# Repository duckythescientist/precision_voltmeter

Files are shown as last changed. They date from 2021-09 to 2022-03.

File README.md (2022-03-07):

# Precision Voltmeter

Partly based off of the Scullcom millivolt meter: http://www.scullcom.uk/design-build-6%c2%bd-digit-millivolt-meter-part-1/

## Serial comms

```
Commands:
    h    - Print this help
    ?    - Print version and date
    r    - Toggle live readout over serial
    p    - Print calibration
    z    - Calibrate at 0V (inputs shorted)
    c... - Calibrate for a specific range and value

Calibration:
    c[n]:[f]  - Calibrates for range [n] with external applied voltage [f]
    Range:
        0: x1 LV
        1: x10
        2: x100
        3: x1000
    Example: to calibrate the x10 range (HV input) with a 4.123V reference,
        the command would be `c1:4.123`
```

# Improvement notes

I added an opto-isolated serial output and spent a weekend tearing down and building back up the circuit. I don't think it's going to get much better than it is (or already was). Without ESD/EMI and environmental noise, the noise in the readings is on the same order of magnitude that I'd expect from thermal noise of a 1Meg resistor. Assuming that my napkin math is correct. Also, the constant offset that I'm seeing is also on the order of what's to be expected with the input bias current of the LTC2057 and a 1Meg resistor. I guess it's just up to software corrections. Still getting around 19-20 usable bits from the ADC. I'm calling that a win.

Environmental noise is still a big issue. Stddev of the readings lowers by an order of magnitude if I sit perfectly still.

# Notes for Future Versions and Improvements

## Issues

The LTC2057 has a common-mode input range from 0.1V below V- to 1.5V _below_ V+. Meaning that with a -2.5V,+5V supply, I can only buffer signals up to 3.5V technically. I'm seeing some sort of latchup-type behavior at around 4.2V. I've bodged in a 6.8V supply rail to the op-amp.

## Bodges

The sampling of the ADC is rather noisy. Adding filter capacitors right at the input and the vref seem to help. Reduced the resistor between the buffer and the ADC to 2.2k. May want to go lower? I'm currently at 100R series from the buffer to the ADC and a 2.2nF cap to gnd.

Adding extra voltage regulator to drive the op-amp positive rail at around 6.8V to give enough common-mode headroom to buffer a full input swing to the ADC.

## Future

The x10 mode presents around a 1Meg input impedance to the op-amp this combined with the couple hundred pA of input bias and offset results in a couple hundred microvolts of DC offset. This has a minimal temperature coefficient up to about 75C but does have a common-mode voltage dependence. I'm not sure what to do to fix it.

A 1Meg input impedance may be the way to go.

For lower noise, it may be nice to try LT3094 and LT3042 for post switching converter regulation. The switching regulator. However, the voltage lines look pretty clean right now. Also, these regulators are pretty expensive and are DFN packages. UPDATE: replacing the switching regulator with batteries didn't measurably reduce the noise. The current design is good enough.

A metal enclosure and/or more shielding could maybe help with environmental noise.

I need a buffer amp for the output of my Kelvin-Varley divider. Or I need a voltage reference below about 4V to calibrate the x1 range. This is a lab problem and not a problem of the voltmeter.

I need to investigate Barbouri's v2 design and see if there is anything worth adding to my design.

# References

## App Notes

Shielding and guarding: https://www.analog.com/media/en/technical-documentation/application-notes/41727248an_347.pdf

Staying well grounded: https://www.analog.com/en/analog-dialogue/articles/staying-well-grounded.html

Millivolt meter PCB: https://www.barbouri.com/2016/05/26/millivolt-meter/ and https://www.barbouri.com/2019/08/07/millivolt-meter-version-2/

EMI filtering for DC-DC converters: https://www.ti.com/lit/an/snva489c/snva489c.pdf

Ferrite beads demystified: https://www.analog.com/en/analog-dialogue/articles/ferrite-beads-demystified.html

Shielding and guarding: https://www.analog.com/media/en/technical-documentation/application-notes/41727248an_347.pdf

PCB guidelines for reduced EMI: https://www.ti.com/lit/an/szza009/szza009.pdf

Overvoltage protection for sensitive amplifier applications: https://www.maximintegrated.com/en/design/technical-documents/app-notes/4/4035.html

Switching low-level signals to a DMM: https://www.ni.com/en-us/innovations/white-papers/06/switching-low-level-signals-to-a-dmm.html

## Datasheets

Voltage reference, ADR4540, used in Scullcom's meter: https://www.analog.com/media/en/technical-documentation/data-sheets/ADR4520_4525_4530_4533_4540_4550.pdf

Voltage reference, MAX6126, used in my meter, kelvin connections: https://datasheets.maximintegrated.com/en/ds/MAX6126.pdf

Negative adjustable voltage regulator, LM337L: https://www.ti.com/lit/ds/symlink/lm337l.pdf

HV low noise zero-drift op-amp, LTC2057, used in my meter: https://www.analog.com/media/en/technical-documentation/data-sheets/2057f.pdf

Zero-drift single-supply rail-to-rail op-amp, AD8628, used in Scullcom's meter: https://www.analog.com/media/en/technical-documentation/data-sheets/AD8628_8629_8630.pdf

ADC 24-bit, LTC2400: https://www.analog.com/media/en/technical-documentation/data-sheets/2400fa.pdf

SPI digital isolator, ADuM3152: https://www.analog.com/media/en/technical-documentation/data-sheets/ADuM3151_3152_3153.pdf

ATmega32U4: https://ww1.microchip.com/downloads/en/DeviceDoc/Atmel-7766-8-bit-AVR-ATmega16U4-32U4_Datasheet.pdf

## Software

64-bit floating point library for AVR-8: https://fp64lib.org/documentation/fp64lib-library-reference/ and https://github.com/fp64lib/fp64lib

MAX7219 7-seg LED driver library: https://github.com/JemRF/max7219

PinChangeInterrupt: https://github.com/NicoHood/PinChangeInterrupt

Statistics library for Arduino: https://github.com/RobTillaart/Statistic

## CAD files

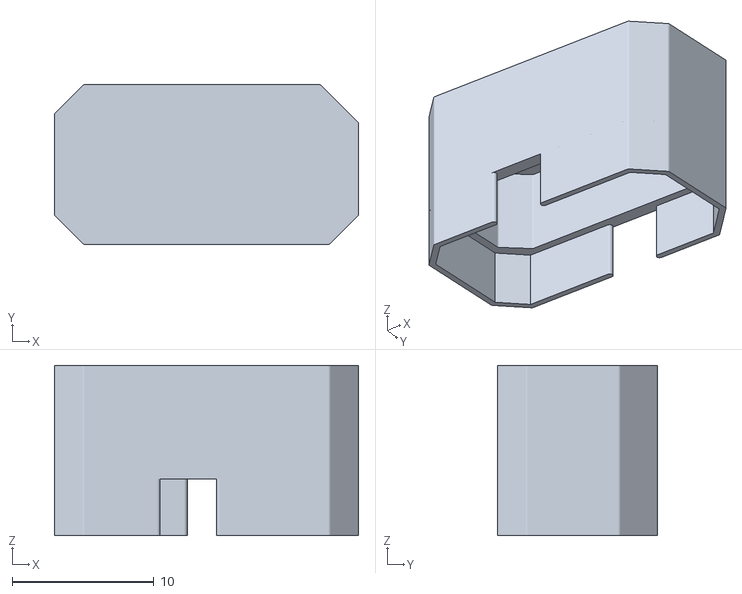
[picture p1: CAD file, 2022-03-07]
vref_cover/vref_cover.stl
21.4 x 11.3 x 12.0

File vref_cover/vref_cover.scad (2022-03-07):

file = "precision_voltmeter-Eco1_User.svg";
ax = 20.64;
ay = 10.79;

offset_r = 0.23;
$fn=100;
difference() {
    translate([-110.48, -112.22, 0]) {
        union() {
            linear_extrude(12)
                offset(r=offset_r)
                    import(file);
            translate([0, 0, 4])
                hull()
                    linear_extrude(8)
                        offset(r=offset_r)
                            import(file);
        }
    }
    #scale([18.5/ax, 8.7/ay, 1 - 2/12])
    translate([-110.48, -112.22, 0]) {
        hull()
            linear_extrude(12)
                offset(r=offset_r)
                    import(file);
    }
}

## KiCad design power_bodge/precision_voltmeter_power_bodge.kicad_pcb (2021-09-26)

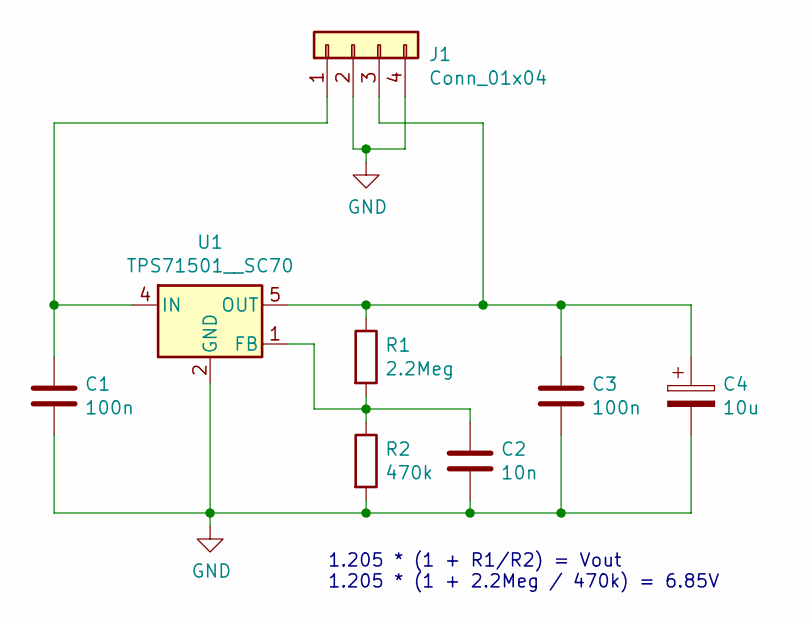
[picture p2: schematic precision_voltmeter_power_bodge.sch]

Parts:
C1, C3: 100n; C_0805_2012Metric_Pad1.18x1.45mm_HandSolder
C2: 10n; C_0805_2012Metric_Pad1.18x1.45mm_HandSolder
C4: 10u; C_0805_2012Metric_Pad1.18x1.45mm_HandSolder
J1: Conn_01x04; PinHeader_1x04_P2.54mm_Vertical
R1: 2.2Meg; R_0805_2012Metric_Pad1.20x1.40mm_HandSolder
R2: 470k; R_0805_2012Metric_Pad1.20x1.40mm_HandSolder
U1: TPS71501__SC70; SOT-353_SC-70-5

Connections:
GND: C1.2, C2.2, C3.2, C4.2, J1.2, J1.4, R2.2, U1.2 (GND)
unnamed: C1.1, J1.1, U1.4 (IN)
unnamed: C2.1, R1.2, R2.1, U1.1 (FB)
unnamed: C3.1, C4.1, J1.3, R1.1, U1.5 (OUT)

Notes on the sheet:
1.205 * (1 + R1/R2) = Vout 1.205 * (1 + 2.2Meg / 470k) = 6.85V

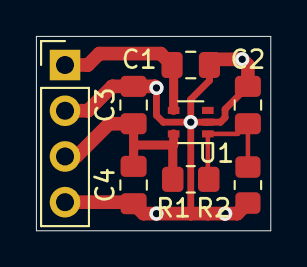
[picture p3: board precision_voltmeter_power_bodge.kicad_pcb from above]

Board: 2 copper layers, 13.0 x 10.8 mm, 8 parts (0 on the bottom side), 4 nets.

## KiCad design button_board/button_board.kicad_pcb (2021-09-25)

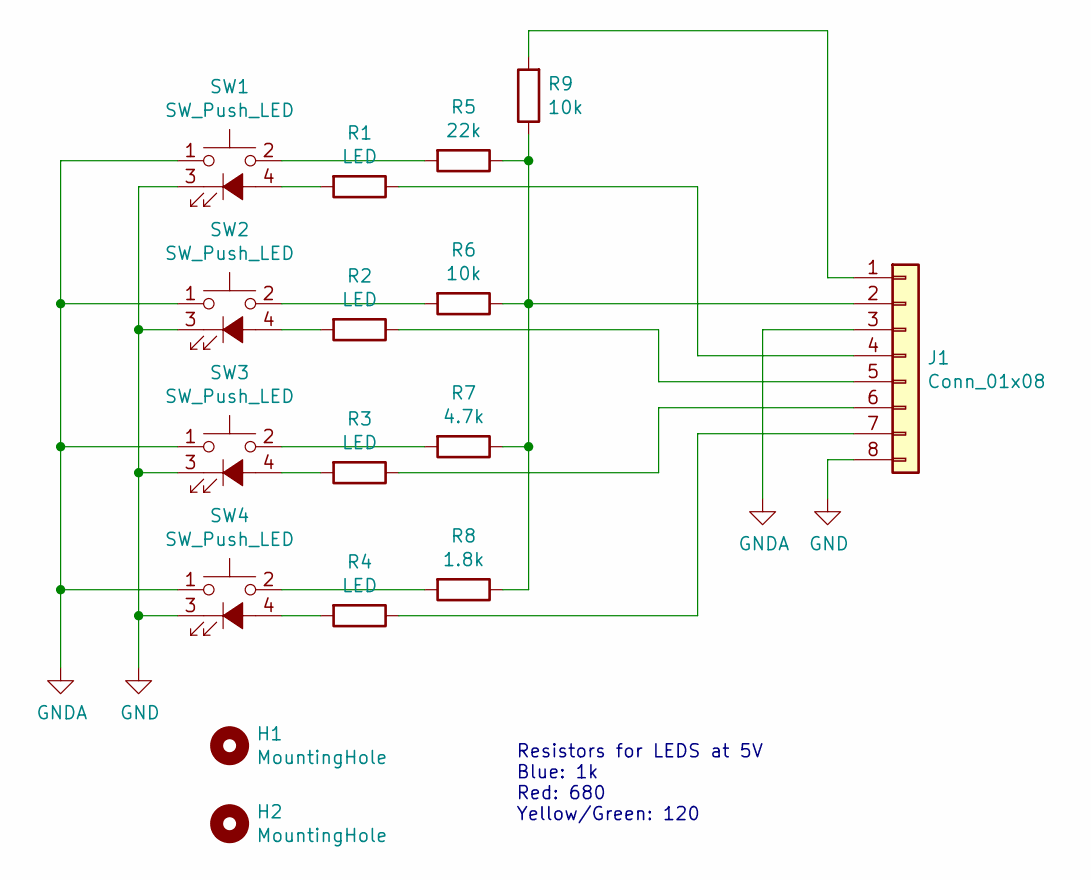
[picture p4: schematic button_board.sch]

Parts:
H1, H2: MountingHole; MountingHole_2.7mm_M2.5
J1: Conn_01x08; PinHeader_1x08_P2.54mm_Vertical
R1, R2, R3, R4: LED; R_0805_2012Metric_Pad1.20x1.40mm_HandSolder
R5: 22k; R_0805_2012Metric_Pad1.20x1.40mm_HandSolder
R6, R9: 10k; R_0805_2012Metric_Pad1.20x1.40mm_HandSolder
R7: 4.7k; R_0805_2012Metric_Pad1.20x1.40mm_HandSolder
R8: 1.8k; R_0805_2012Metric_Pad1.20x1.40mm_HandSolder
SW1, SW2, SW3, SW4: SW_Push_LED; tactile-push-button-illuminated_ILS_TA180

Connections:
GND: J1.8, SW1.3 (K), SW2.3 (K), SW3.3 (K), SW4.3 (K)
GNDA: J1.3, SW1.1, SW2.1, SW3.1, SW4.1
unnamed: J1.1, R9.2
unnamed: J1.2, R5.1, R6.1, R7.1, R8.1, R9.1
unnamed: J1.4, R1.1
unnamed: J1.5, R2.1
unnamed: J1.6, R3.1
unnamed: J1.7, R4.1
unnamed: R1.2, SW1.4 (A)
unnamed: R2.2, SW2.4 (A)
unnamed: R3.2, SW3.4 (A)
unnamed: R4.2, SW4.4 (A)
unnamed: R5.2, SW1.2
unnamed: R6.2, SW2.2
unnamed: R7.2, SW3.2
unnamed: R8.2, SW4.2

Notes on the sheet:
Resistors for LEDS at 5V Blue: 1k Red: 680 Yellow/Green: 120

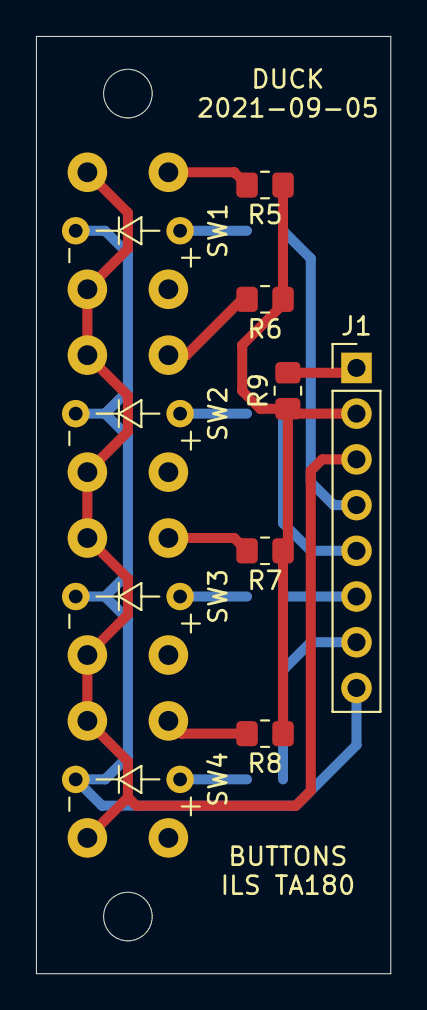
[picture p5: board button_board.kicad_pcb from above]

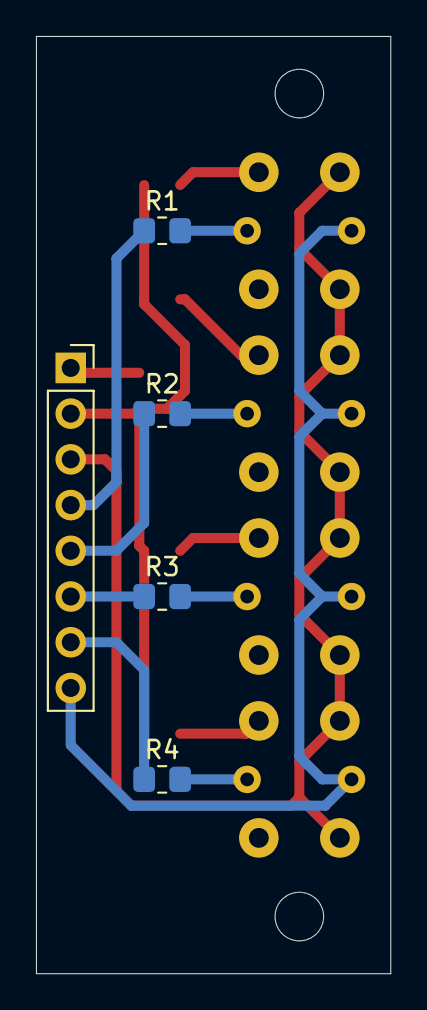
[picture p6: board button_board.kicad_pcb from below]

Board: 2 copper layers, 19.7 x 52.1 mm, 16 parts (4 on the bottom side), 16 nets.

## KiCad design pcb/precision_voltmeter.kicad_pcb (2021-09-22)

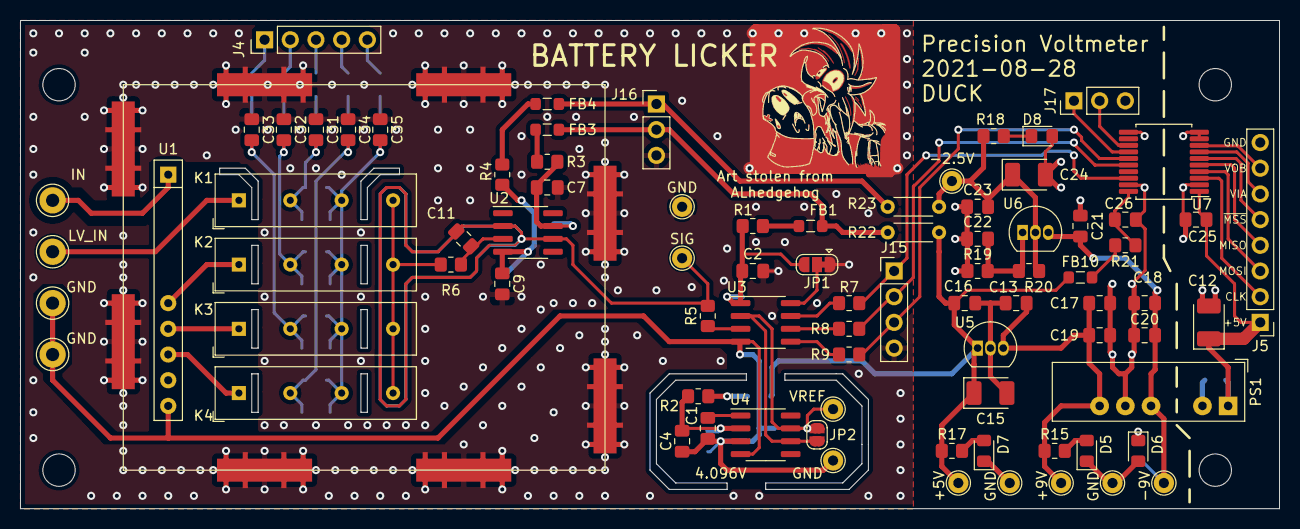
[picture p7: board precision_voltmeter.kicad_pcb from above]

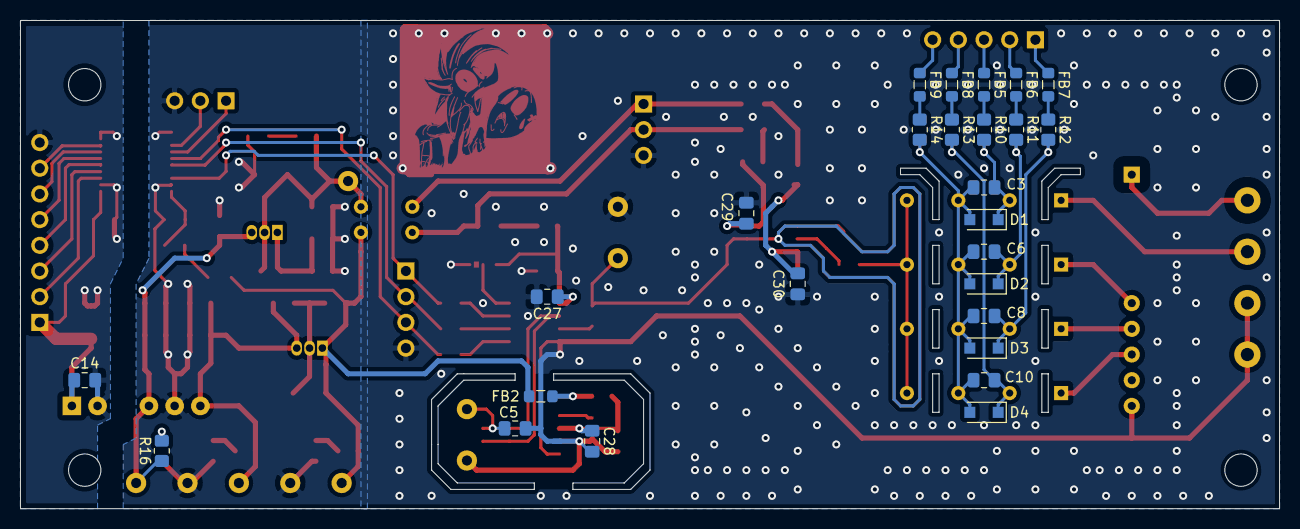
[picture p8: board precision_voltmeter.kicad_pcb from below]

Board: 2 copper layers, 124.5 x 48.3 mm, 121 parts (26 on the bottom side), 63 nets.

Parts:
C1, C2, C3, C4, C5, C6, C7, C8, C9, C10, C13, C14, C16, C19, C20, C21, C22, C23, C25, C26, C31, C32, C33, C34: 100n; C_0805_2012Metric_Pad1.18x1.45mm_HandSolder
C11: DNP 220p; C_0805_2012Metric_Pad1.18x1.45mm_HandSolder
C12, C15, C24: 4.7u; CP_EIA-3528-12_Kemet-T_Pad1.50x2.35mm_HandSolder
C17, C18: 1u; C_0805_2012Metric_Pad1.18x1.45mm_HandSolder
C27, C28, C29, C30: 10u; C_0805_2012Metric_Pad1.18x1.45mm_HandSolder
C35: 5x 100n; C_0805_2012Metric_Pad1.18x1.45mm_HandSolder
D1, D2, D3, D4: 1n4148; D_SOD-123F
D5, D6, D7, D8: LED; LED_0805_2012Metric_Pad1.15x1.40mm_HandSolder
FB1, FB2, FB3, FB4, FB5, FB6, FB7, FB8, FB9, FB10: Bead; L_0805_2012Metric_Pad1.05x1.20mm_HandSolder
H1, H2, H3, H4: MountingHole; MountingHole_3.2mm_M3
J1: IN_PLUS; Pin_D1.3mm_L11.0mm
J2, J14: IN_MINUS; Pin_D1.3mm_L11.0mm
J3: IN_PLUS_LV; Pin_D1.3mm_L11.0mm
J4: Conn_01x05; PinHeader_1x05_P2.54mm_Vertical
J5: Conn_01x08; PinHeader_1x08_P2.54mm_Vertical
J6, J7, J8, J9, J10, J11, J12, J13: shield clip; smt_rfi_clip_S2711-46R
J15: Conn_01x04; PinHeader_1x04_P2.54mm_Vertical
J16, J17: Conn_01x03; PinHeader_1x03_P2.54mm_Vertical
JP1: 50/60Hz select; SolderJumper-3_P1.3mm_Bridged12_RoundedPad1.0x1.5mm
JP2: Jumper_NO_Small; SolderJumper-2_P1.3mm_Open_RoundedPad1.0x1.5mm
K1, K2, K3, K4: COTO-1839-108N; Relay_SPST_StandexMeder_SIL_Form1A
PS1: 5V in +/-9V out; Converter_DCDC_XP_POWER-IAxxxxS_THT
R1, R2, R3, R4, R11, R12, R13, R14: 10R; R_0805_2012Metric_Pad1.20x1.40mm_HandSolder
R5: 4.7k; R_0805_2012Metric_Pad1.20x1.40mm_HandSolder
R6: 1.2k; R_0805_2012Metric_Pad1.20x1.40mm_HandSolder
R7, R8: 33; R_0805_2012Metric_Pad1.20x1.40mm_HandSolder
R9: 3x 33R; R_0805_2012Metric_Pad1.20x1.40mm_HandSolder
R10: 5x 10R; R_0805_2012Metric_Pad1.20x1.40mm_HandSolder
R15, R16: 1k; R_0805_2012Metric_Pad1.20x1.40mm_HandSolder
R17, R18: 470; R_0805_2012Metric_Pad1.20x1.40mm_HandSolder
R19, R20: 240; R_0805_2012Metric_Pad1.20x1.40mm_HandSolder
R21: 2.2R; R_0805_2012Metric_Pad1.20x1.40mm_HandSolder
R22, R23: 0; R_Axial_DIN0204_L3.6mm_D1.6mm_P5.08mm_Horizontal
TP1: vref; TestPoint_THTPad_D2.0mm_Drill1.0mm
TP2, TP3, TP4, TP6: gnd; TestPoint_THTPad_D2.0mm_Drill1.0mm
TP5: sig_buffered; TestPoint_THTPad_D2.0mm_Drill1.0mm
TP7, TP8, TP9, TP10: TestPoint; TestPoint_THTPad_D2.0mm_Drill1.0mm
U1: Caddock_resistor_network_1776-C68; R_Array_SIP10-6
U2: LTC2057/AD8628; SOIC-8_3.9x4.9mm_P1.27mm
U3: LTC2400CS8PBF; SOIC-8_3.9x4.9mm_P1.27mm
U4: MAX6126/ADR4540; SOIC-8_3.9x4.9mm_P1.27mm
U5: L78L05_TO92; TO-92_Inline
U6: LM337L_TO92; TO-92_Inline
U7: ADUM3152; SSOP-20_5.3x7.2mm_P0.65mm

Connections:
+5V: C15.1, C16.1, FB1.1, FB2.1, FB3.1, FB10.1, J16.2, R17.1, R22.1, R22.2, TP8.1, U5.1
+5VP: C12.1, C14.1, C25.1, J5.1, PS1.1, U7.1
+9V: C13.1, C17.1, C19.1, PS1.6, R15.1, TP7.1, U5.3
-2V5: C23.2, C24.1, FB4.1, J16.1, R18.1, R20.2, R23.1, R23.2, TP10.1, U6.2
-9V: C18.1, C20.1, C21.2, PS1.4, R16.1, TP9.1, U6.3
/VCC_ADC: C2.1, C27.1, JP1.3, R1.2, U3.1
/VCC_OPAMP: C7.1, C29.1, R3.2, U2.7
/VCC_REF: C4.1, C28.1, R2.2, U4.2
/VSS_OPAMP: C9.1, C30.1, R4.2, U2.4
GND: C1.2, C2.2, C4.2, C5.2, C7.2, C9.2, C13.2, C15.2, C16.2, C17.2, C18.2, C19.2, C20.2, C21.1, C22.1, C23.1, C24.2, C26.2, C27.2, C28.2, C29.2, C30.2, C31.1, C32.1, C33.1, C34.1, C35.1, D5.1, D6.2, D7.1, D8.2, J2.1, J6.1, J7.1, J8.1, J9.1, J10.1, J11.1, J12.1, J13.1, J14.1, J15.4, J16.3, J17.3, JP1.1, PS1.5, R19.1, TP2.1, TP3.1, TP4.1, TP6.1, U1.10, U3.4, U4.3, U4.4, U5.2, U7.11, U7.19
GNDPWR: C12.2, C14.2, C25.2, J5.8, PS1.2, U7.2, U7.9, U7.10
MISO: J15.2, R8.1, U7.16
unnamed: C1.1, U4.1
unnamed: C3.2, C31.2, D1.1, K1.3, R10.2
unnamed: C5.1, JP2.1, JP2.2, TP1.1, U3.2, U4.6, U4.7
unnamed: C3.1, C6.1, C8.1, C10.1, C35.2, D1.2, D2.2, D3.2, D4.2, K1.5, K2.5, K3.5, K4.5, R14.2
unnamed: C10.2, C34.2, D4.1, K4.3, R13.2
unnamed: C11.1, R5.2, TP5.1, U2.2, U2.6
unnamed: C11.2, R6.1, U2.3
unnamed: C22.2, R19.2, R20.1, U6.1
unnamed: C26.1, R21.2, U7.20
unnamed: C6.2, C32.2, D2.1, K2.3, R11.2
unnamed: C8.2, C33.2, D3.1, K3.3, R12.2
unnamed: D5.2, R15.2
unnamed: D6.1, R16.2
unnamed: D7.2, R17.2
unnamed: D8.1, R18.2
unnamed: FB1.2, R1.1
unnamed: FB2.2, R2.1
unnamed: FB3.2, R3.1
unnamed: FB4.2, R4.1
unnamed: FB5.1, J4.3
unnamed: FB5.2, R10.1
unnamed: FB6.1, J4.2
unnamed: FB6.2, R11.1
unnamed: FB7.1, J4.1
unnamed: FB7.2, R12.1
unnamed: FB8.1, J4.4
unnamed: FB8.2, R13.1
unnamed: FB9.1, J4.5
unnamed: FB9.2, R14.1
unnamed: FB10.2, R21.1
unnamed: J1.1, U1.1
unnamed: J3.1, K1.1
unnamed: J5.2, U7.3
unnamed: J5.3, U7.4
unnamed: J5.4, U7.5
unnamed: J5.5, U7.6
unnamed: J5.6, U7.7
unnamed: J5.7, U7.8
unnamed: J17.1, U7.14
unnamed: J17.2, U7.13
unnamed: JP1.2, U3.8
unnamed: K1.7, K2.7, K3.7, K4.7, R6.2
unnamed: K2.1, U1.6
unnamed: K3.1, U1.7
unnamed: K4.1, U1.8
unnamed: R5.1, U3.3
unnamed: R7.2, U3.7
unnamed: R8.2, U3.6
unnamed: R9.2, U3.5
SCK: J15.1, R7.1, U7.18
nCS: J15.3, R9.1, U7.15

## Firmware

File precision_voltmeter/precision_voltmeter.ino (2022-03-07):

/*
   Architecture:
   ADC 24-bit over SPI: LTC2400
   Voltage reference 4.096V: MAX6126 or ADR4540
   Divider, switched by relays: Caddock 1776-C68
       x1, x10, x100, x1000

   UI:
   Display 8-digit 7-segment: MAX7219
   Buttons:
       AUTO: fixed vs auto ranging
       AVG: change averaging settings
       HOLD: min/max hold



*/

#include <stdio.h>
#include <stdint.h>
#include <util/delay.h>
#include <avr/sleep.h>
#include <avr/power.h>
#include <fp64lib.h>
#include <PinChangeInterrupt.h> // https://github.com/NicoHood/PinChangeInterrupt
#include <Statistic.h> // https://github.com/RobTillaart/Statistic

#include "double.h"
#include "max7219.h"
#include "freememory.h"
#include "cal.h"


#define ADC_nCS 16
#define ADC_SDO 14
#define ADC_SCK 15

// Arduino needs declarations with default arguments in the main .ino file
uint32_t ltc2400_read(uint8_t ncs = ADC_nCS, uint8_t sdo = ADC_SDO, uint8_t sck = ADC_SCK);


#define LED1 3
#define LED2 5
#define LED3 6
#define LED4 9
uint8_t led_pins[] = {LED1, LED2, LED3, LED4};

#define BUTTON_PIN A8

//#define MAX_CLK 18
//#define MAX_CS 19
//#define MAX_DIN 20
MAX7219 max7219;

enum Range : uint8_t {RANGE_AUTO = 0, RANGE_x1, RANGE_x10, RANGE_x100, RANGE_x1k, RANGE_NONE};
enum Range range_mode = RANGE_x1k;
enum Range relay_mode = RANGE_NONE;

#define RELAY_x100 A3
#define RELAY_x10  10
#define RELAY_x1   2
#define RELAY_x1k  4


#define ALPHA_2Hz (0.6262344812602125f)
#define ALPHA_0p2Hz (0.14350373836394034f)
#define ALPHA_0p05Hz (0.04020288254460277f)

enum AveragingMode : uint8_t {AVERAGE_NONE = 0, AVERAGE_FAST, AVERAGE_SLOW, AVERAGE_SUPER_SLOW, AVERAGING_MODES_COUNT} averaging_mode = AVERAGE_NONE;
Double averaged;

bool interrupt_happened = false;

bool readout_enabled = true;

Statistic stats;



void set_relays(enum Range mode) {
  digitalWrite(RELAY_x1, mode == RANGE_x1);
  digitalWrite(RELAY_x10, mode == RANGE_x10);
  digitalWrite(RELAY_x100, mode == RANGE_x100);
  digitalWrite(RELAY_x1k, mode == RANGE_x1k);
}


void setup() {
  Serial.begin(115200);
  Serial1.begin(115200);
  pinMode(LED1, OUTPUT);
  digitalWrite(LED1, LOW);
  pinMode(LED2, OUTPUT);
  digitalWrite(LED2, LOW);
  pinMode(LED3, OUTPUT);
  digitalWrite(LED3, LOW);
  pinMode(LED4, OUTPUT);
  digitalWrite(LED4, LOW);
  pinMode(BUTTON_PIN, INPUT);


  pinMode(ADC_nCS, OUTPUT);
  digitalWrite(ADC_nCS, HIGH);
  pinMode(ADC_SDO, INPUT);
  pinMode(ADC_SCK, OUTPUT);
  digitalWrite(ADC_SCK, LOW);

  pinMode(RELAY_x1, OUTPUT);
  pinMode(RELAY_x10, OUTPUT);
  pinMode(RELAY_x100, OUTPUT);
  pinMode(RELAY_x1k, OUTPUT);
  relay_mode = RANGE_x1k;
  set_relays(relay_mode);

  max7219.Begin();
  max7219.MAX7219_SetBrightness(0x5);  // 0x0 - 0xF
  max7219.Clear();
  max7219.DisplayText("hEllo", 0);
  Serial.println("hello");
  Serial1.println("hello");
  delay(1000);
  load_calibration();
  print_cal();
  if (!current_calibration.calibrated) {
    Serial.println(F("UNCALIBRATED"));
    max7219.Clear();
    max7219.DisplayText("UnCAL", 0);
    delay(3000);
  }

   // Putting the processor to sleep messes with updates
   // so wait here while button 1 is held.
   while (read_buttons() == 1) {
     delay(5000);
     Serial.println(F("Waiting for update"));
   }

}


void update_average(Double val) {
  switch (averaging_mode) {

    case AVERAGE_FAST:
      averaged += (val - averaged) * Double(ALPHA_2Hz);
      break;
    case AVERAGE_SLOW:
      averaged += (val - averaged) * Double(ALPHA_0p2Hz);
      break;
    case AVERAGE_SUPER_SLOW:
      averaged += (val - averaged) * Double(ALPHA_0p05Hz);
      break;
    case AVERAGE_NONE:
    default:
      averaged = val;
      break;
  }
}
//float get_iir_alpha(float f, float sampling_period=0.13333f) {
//  float foo = TWO_PI * sampling_period * f;
//  return foo / (1 + foo);
//}

//import math
//def get_iir_alpha(f, sampling_period=0.13333):
//    foo = 2 * math.pi * sampling_period * f
//    return foo / (1 + foo)




void update_range_mode(enum Range mode) {
  // Change hardware for new range_mode
  range_mode = mode;
  digitalWrite(LED1, LOW);
  digitalWrite(LED3, LOW);
  switch (range_mode) {
    case RANGE_x10:
      Serial.println(F("Range x10"));
      relay_mode = RANGE_x10;
      break;
    case RANGE_x100:
      Serial.println(F("Range x100"));
      relay_mode = RANGE_x100;
      break;
    case RANGE_x1k:
      Serial.println(F("Range x1k"));
      relay_mode = RANGE_x1k;
      break;
    case RANGE_x1:
    Serial.println(F("DANGER RANGE x1"));
        digitalWrite(LED3, HIGH);
        relay_mode = RANGE_x1;
        break;
    case RANGE_AUTO:  // FALLTHROUGH
    default:
      Serial.println(F("Range AUTO"));
      digitalWrite(LED1, HIGH);
      relay_mode = RANGE_x1k;
      break;
  }
  set_relays(relay_mode);
}


void print_help() {
  Serial.println(F(
    "Commands:\r\n"
    "\th    - Print this help\r\n"
    "\t?    - Print version and date\r\n"
    "\tr    - Toggle live readout over serial\r\n"
    "\tp    - Print calibration\r\n"
    "\tz    - Calibrate at 0V (inputs shorted)\r\n"
    "\tc... - Calibrate for a specific range and value\r\n"
    "\r\n"
    "Calibration:\r\n"
    "\tc[n]:[f]  - Calibrates for range [n] with external applied voltage [f]\r\n"
    "\tRange:\r\n"
    "\t\t0: x1 LV\r\n"
    "\t\t1: x10\r\n"
    "\t\t2: x100\r\n"
    "\t\t3: x1000\r\n"
    "\tExample: to calibrate the x10 range (HV input) with a 4.123V reference,\r\n"
    "\t\tthe command would be `c1:4.123`\r\n"
  ));
}


void handle_serial() {
  int cal_mode = 0;
  float64_t real_value = float64_ONE_POSSIBLE_NAN_REPRESENTATION;
  char buf[32];
  size_t len;
  int command = Serial.read();
  if (command >= 'A' && command <= 'Z') {
    command ^= 0x20;
  }
  switch (command) {
    case 'h':
      readout_enabled = false;
      print_help();
      break;
    case '?':
      readout_enabled = false;
      Serial.println(F("Precision Voltmeter"));
      Serial.print(F("\tVersion: "));
      Serial.println(CAL_VERSION, HEX);
      Serial.println(F("\tDate: " __DATE__));
      Serial.println(F("Type h for help"));
      break;
    case 'r':
      readout_enabled = !readout_enabled;
      break;
    case 'p':
      print_cal();
      break;
    case 'z':
      zero_cal();
      break;
    case 'c':
      cal_mode = Serial.read();
      if (cal_mode < '0' || cal_mode > '3') {
        Serial.print(F("Bad cal mode "));
        Serial.println(cal_mode);
        return;
      }
      cal_mode = cal_mode - '0';
      if (Serial.read() != ':') {
        Serial.println(F("Format error"));
        return;
      }
      len = Serial.readBytesUntil('\n', buf, sizeof(buf));
      if (!len) {
        Serial.println(F("Failed to read number"));
        return;
      }
      real_value = fp64_atof(buf);
      if (fp64_isfinite(real_value)) {
        cal_at_value(static_cast<Range>(cal_mode + 1), real_value);
      }
      else {
        Serial.println(F("Bad number"));
      }
      break;
    case ' ':
    case '\r':
    case '\n':
      break;
    default:
      Serial.print(F("Unk cmd:"));
      Serial.println(command, HEX);
      break;
  }
}

void update_stability(int32_t raw) {
  static int32_t last_raw_reading = 0;
  static uint32_t inc_mask = 0;
  static uint8_t inc_count = 0;

  uint8_t increasing = (raw > last_raw_reading) ? 1 : 0;
  last_raw_reading = raw;
  if (inc_mask & 0x80000000UL) {
    inc_count -= 1;
  }
  inc_mask <<= 1;
  inc_mask |= increasing;
  inc_count += increasing;
  // A truly binomial process will be between 13/32 and 19/32
  // inclusive 78% of the time. This is maybe too forgiving.
  // 14-18 inclusive: 62%
  // 15-17 inclusive: 40%
  // 16 exactly: 14%
  if (inc_count >= (16 - 3) && inc_count <= (16 + 3)) {
    digitalWrite(LED4, HIGH);
  }
  else {
    digitalWrite(LED4, LOW);
  }
}

void loop() {
  static int last_button = 0;
  

  //  int mem = freeMemory();
  //  Serial.print("freemem:");
  //  Serial.println(mem);

  if (Serial.available() > 0) {
    handle_serial();
  }

  int button = read_buttons();
  if (button && button != last_button) {
    Serial.print("Button pressed: ");
    Serial.println(button);

    if (button == 1) {
      // Update range_mode
      switch (range_mode) {
        case RANGE_AUTO:
          range_mode = RANGE_x10;
          break;
        case RANGE_x10:
          range_mode = RANGE_x100;
          break;
        case RANGE_x100:
          range_mode = RANGE_x1k;
          break;
        case RANGE_x1k: // FALLTHROUGH
        default:
          range_mode = RANGE_AUTO;
          break;
      }
      update_range_mode(range_mode);
    }

    if (button == 2) {
      averaging_mode = static_cast<AveragingMode>((averaging_mode + 1) % AVERAGING_MODES_COUNT);
      switch (averaging_mode) {
        case AVERAGE_FAST:
          Serial.println(F("Avg fast"));
          analogWrite(LED2, 16);
          break;
        case AVERAGE_SLOW:
          Serial.println(F("Avg slow"));
           analogWrite(LED2, 64);
          break;
        case AVERAGE_SUPER_SLOW:
          Serial.println(F("Avg SUPER slow"));
          digitalWrite(LED2, HIGH);
          break;
        case AVERAGE_NONE:  // FALLTHROUGH
        default:
          Serial.println(F("Avg none"));
          digitalWrite(LED2, LOW);
          break;
      }
    }

    if (button == 3) {
      if (range_mode != RANGE_x1) {
        update_range_mode(RANGE_x1);
      }
      else {
        update_range_mode(RANGE_AUTO);
      }

    }

    if (button == 4) {
      // not currently handled
    }

    if (button == 5) {
      digitalWrite(LED3, HIGH);
      digitalWrite(LED4, HIGH);
      delay(3000);
      button = read_buttons();
      if (button == 5) {
        digitalWrite(LED3, LOW);
        digitalWrite(LED4, LOW);
        digitalWrite(LED1, HIGH);
        digitalWrite(LED2, HIGH);
        while (read_buttons());
        zero_cal();
      }
      else {
        digitalWrite(LED3, HIGH);
        digitalWrite(LED4, HIGH);
      }
    }
  }
  last_button = button;

  uint32_t reading = ltc2400_read();
  int32_t raw = ltc2400_convert_raw(reading);
  float float_norm = ltc2400_adjust_float_norm(raw);
  Double voltage = ltc2400_adjust(raw, relay_mode);
  char buf[16] = {0};
  snprintf(buf, 32, "Raw: 0x%08lx ", raw);
  if (readout_enabled) {
    Serial.print(buf);
    Serial.println(float_norm, 7);
  }
  update_average(voltage);
  update_stability(raw);
  Serial1.print(buf);
  Serial1.print(float_norm, 7);
  Serial1.print(" ");
  display_value(averaged, range_mode);

  if (range_mode == RANGE_AUTO) {
    // Check if outside of range
    if (float_norm < -0.06 || float_norm > 1.1) {
      // Could step up by one level, but going straight to x1k works too.
      relay_mode = RANGE_x1k;
      set_relays(relay_mode);
      // Throw out the current conversion
      ltc2400_read();
    }
    // Should we increase sensitivity?
    else if (float_norm > -0.005 && float_norm < 0.09) {
      switch (relay_mode) {
        case RANGE_x1k:
          Serial.println(F("Inc x100"));
          relay_mode = RANGE_x100;
          set_relays(relay_mode);
          break;
        case RANGE_x100:
          Serial.println(F("Inc x10"));
          relay_mode = RANGE_x10;
          set_relays(relay_mode);
          break;
        case RANGE_x10:
          // Don't go to x1 sensitivity automatically
          break;
        default:
          // Only here if something went wrong in the code
          Serial.println(F("Fail. Range x1k"));
          relay_mode = RANGE_x1k;
          set_relays(relay_mode);
          break;
      }
    }
  }


  bool error = false;
  if (range_mode != RANGE_AUTO) {
    if (float_norm < -0.073) {
      max7219.DisplayText("-UndEr  ", 0);
      error = true;
    }
    if (float_norm > 1.12) {
      max7219.DisplayText("OVEr    ", 0);
      error = true;
    }
  }
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

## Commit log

2021-09-22 Add initial working files
    [precision_voltmeter.kicad_pcb, precision_voltmeter.sch, precision_voltmeter_SHEET_power.sch]
2021-09-25 SCH ONLY, add bodge filter caps
    [precision_voltmeter.sch]
2021-09-25 Add cal printing and button combo
2021-09-25 Add button board files
    [button_board.kicad_pcb, button_board.sch]
2021-09-26 Add power bodge board
    [precision_voltmeter.sch, precision_voltmeter_power_bodge.kicad_pcb, precision_voltmeter_power_bodge.sch]
2021-09-26 Add calibration (for non-zero) and super slow averaging
    Also fix a bug with the display maths
2022-03-07 Add 3d printable vref cover
    [vref_cover.scad, vref_cover.stl]
